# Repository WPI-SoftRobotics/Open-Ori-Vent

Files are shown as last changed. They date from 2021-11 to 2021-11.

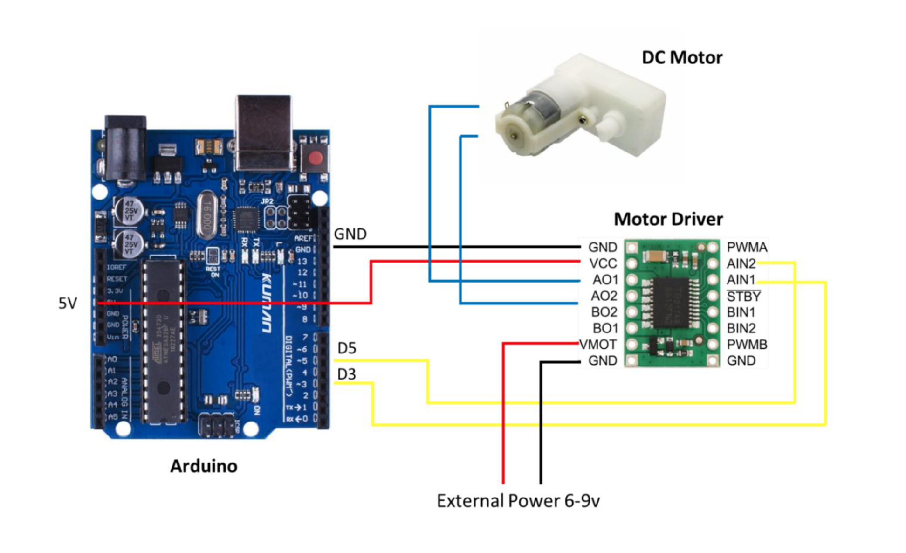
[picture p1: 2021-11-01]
images/wiring_diagram.png

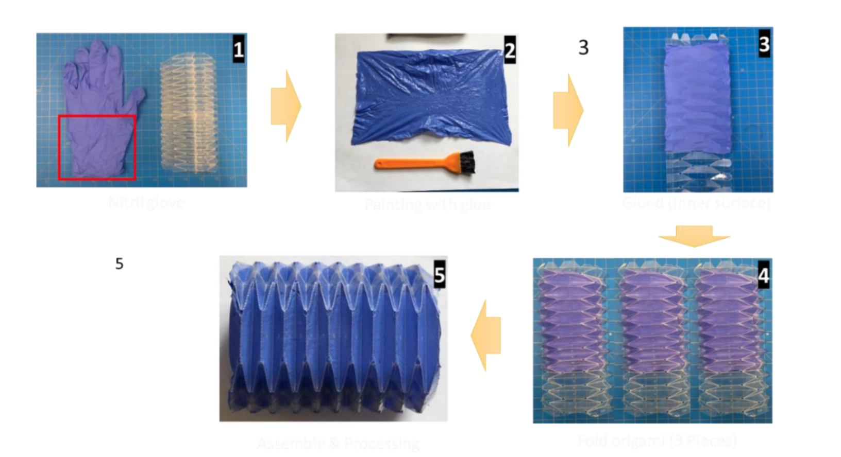
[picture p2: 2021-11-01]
images/sealing_method_2.png

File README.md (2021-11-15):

# Open-Ori-Vent: Portable Origami-Inspired Ventilators

The COVID-19 pandemic is responsible for hundreds of thousands of deaths
worldwide and remains a challenge that humanity must still overcome. As
hospitals continue to admit critical patients, they face medical
equipment shortages that may hinder life-saving treatments. We seek to
combat this equipment shortage by presenting a proof-of-concept portable
automated ventilator that is:

-   Low cost

-   Simple, Lightweight, Easy-to fabricate

As an open-source project, we are sharing all the CAD files as well
as the software. We hope that you can also make your own ventilator
using these instructions! For the current designs, laser cutters and 3d
printers are necessary, though these parts could be cut/printed
elsewhere and then mailed to you for assemble.

## Disclaimer
:warning: We would like include a warning and disclaimer here:

Please check the full disclaimer as well before proceeding.

* The material and documentation here is provided with no warranties explicit or implied.
* No material on this site is intended to provide medical advice. All designs are intended for investigational use only.
* This site does not represent any official policies or procedures.

The project is provided "as is", without warranty of any kind, express or implied, including but not limited to the warranties of merchantability, fitness for a particular purpose and noninfringement.

In no event shall the authors or copyright holders be liable for any claim, damages or other liability, whether in an action of contract, tort or otherwise, arising from, out of or in connection with the software or the use or other dealings in the software.

Only use **this repository, designs, documentation or any provided information** if you accept the above disclaimer.

## Citation:

Ori-Vent: Design and Prototyping of Accessible and Portable Origami-Inspired Ventilators

Please cite: 
> Aihaitijiang, Abudula, et al. "Ori-Vent: Design and Prototyping of Accessible and Portable Origami-Inspired Ventilators." *International Symposium on Experimental Robotics.* Springer, Cham, 2020.

WPI Soft Robotics Lab [softrobotics.wpi.edu](https://softrobotics.wpi.edu/)

Worcester Polytechnic Institute

## Materials and methods
See tutorials in our project [Wiki](https://github.com/WPI-SoftRobotics/Open-Ori-Vent/wiki). Or download ReadMe.pdf

## Download 

git clone the whole project or download .zip file (Include all Steps)

## Video

See here: [https://youtu.be/49nRoLKjMFs](https://youtu.be/49nRoLKjMFs)

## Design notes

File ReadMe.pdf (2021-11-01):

## Open-Source Project

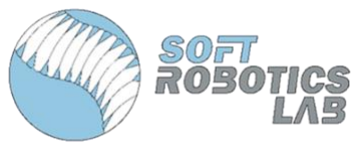
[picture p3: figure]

# Ori-Vent: Design and Prototyping of Accessible and Portable Origami-Inspired Ventilators

## Soft Robotics Lab

## Worcester Polytechnic Institute

Table of Contents

Introduction ------------------------------------------------------------------------------------ 2

Part 1: Materials ------------------------------------------------------------------------------- 2

Part 2: Printed Parts List --------------------------------------------------------------------- 3

Part 3: Building the Bellows ----------------------------------------------------------------- 4

Part 4: Sealing Bellows ----------------------------------------------------------------------- 5

Part 5: Wiring Diagram ----------------------------------------------------------------------- 6

Part 6: Assembly ------------------------------------------------------------------------------- 7

Part 7: Download Section --------------------------------------------------------------------7

Part 8: Video ------------------------------------------------------------------------------------ 7

Introduction:

The COVID-19 pandemic is responsible for hundreds of thousands of deaths worldwide and remains a challenge that humanity must still overcome. As hospitals continue to admit critical patients, they face medical equipment shortages that may hinder life-saving treatments. We seek to combat this equipment shortage by presenting a proof-of-concept portable automated ventilator that is:

- Low cost
- Simple, Lightweight, Easy-to fabricate

As an open-source project, we will made public all the CAD files as well as the software. We hope that you can also make your own ventilator using these instructions! For the current designs, laser cutters and 3d printers are necessary, though these parts could be cut/printed elsewhere and then mailed to you for assemble.

Part 1: Materials & Orders

The initial prototype uses inexpensive materials and is easy to manufacture. It is not necessary to buy or order same product as listed below. You can do substitutions from your own supplies or purchase similar items from somewhere else.

1 x Arduino | $10.69 | Order (https://www.amazon.com/kuman-Board-ATmega328P-Cable-Arduino/dp/B016D5KOOC?s=electronics) (Amazon)
1 x Jumper Wires | $3.95 | Order (https://www.amazon.com/Adafruit-Premium-Female-Extension-Jumper/dp/B011OCHYH4) (Amazon)
1 x Gear Motor | $5.75 | Order (https://www.robotshop.com/en/solarbotics-gm2-gear-motor-2-offset.html) (RobotShop)
1 x Motor Driver | $3.33 | Order (https://www.robotshop.com/en/pololu-dual-dc-motor-driver-1a-4-5v-3-5v-tb6612fng.html) (RobotShop)
1 x Pressure Sensor (optional) | $16.33 | Order (https://www.digikey.com/en/products/detail/nxp-usa-inc/mpx5010dp/464054) (Digi-Key)

For sealing origami bellows:

1 x *Stretchlon200 Bagging Film | $3.90 | Order (https://www.fibreglast.com/product/stretchlon-200-bagging-film-1678/Vacuum_Bagging_Films_Peel_Ply_Tapes) (FibreGlast)
1 x *Nitrile Exam Gloves (Optional) | - | Order (https://www.amazon.com/MedPride-Powder-Free-Nitrile-Gloves-Medium/dp/B00GS8W3T4) (Amazon)
1 x *E6000 Glue | $7.64 | Order (https://www.amazon.com/E6000-230010-Craft-Adhesive-Ounces/dp/B007TSYNG8) (Amazon)

Others:

1 x Screws | - | -
1 x *PET film | - | -
1 x One way valve (2 Pieces) | $6.69 | Order (https://www.amazon.com/Check-Valve-Inline-Return-Liquid/dp/B07CC9K599) (Amazon)
1 x Fishing wire | $2.99 | Order (https://www.amazon.com/Triple-Fish-Test-Leader-Fishing/dp/B01BZPPDJG?rnid=386589011) (Amazon)
1 x Rubber Tube | $8.59 | Order (https://www.amazon.com/Nydotd-Natural-Slingshot-Catapult-Surgical/dp/B07DL6JJZ2) (Amazon)

* Optional Part: Order if you want to make origami bellows.

Part 2: Printed Part List

Files: Open Source Ori-Vent\Printed Parts\.STL & .SLDPRT

Here is a list of all the parts that need to be printed:

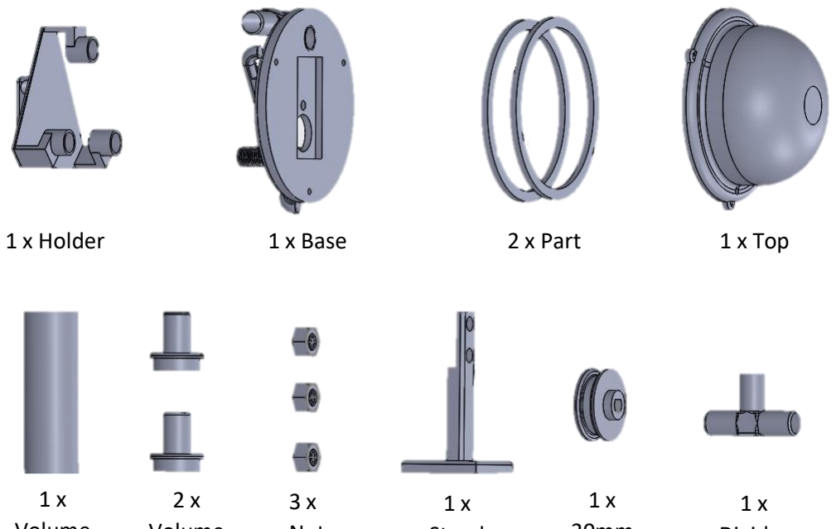
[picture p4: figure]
1 x Holder; 1 x Base; 2 x Part; 1 x Top

Print Settings

Profile Default: High resolution

Supports: Yes

Infill: 60%+

Filament material: PLA

Volume
Tube

Volume
(in&out)

Nut
Stand

30mm
Spool

Divider

Part 3: Building the Bellows

Origami Bellows:

Files: Open Source Ori-Vent\Origami_Laser Cut\.DXF

Quantity: 3 x Origami Pattern

Material: PET (Polyethylene Terephthalate) or any other low-cost and accessible plastic

Note: We provide two different length of origami patterns (18 inch and 9)

3D Printed Bellows

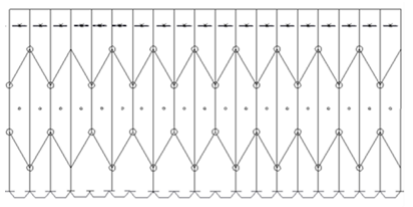
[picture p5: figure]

Files: Open Source Ori-Vent \ 3D Printed Bellows \ .SLDPRT:

Print Settings

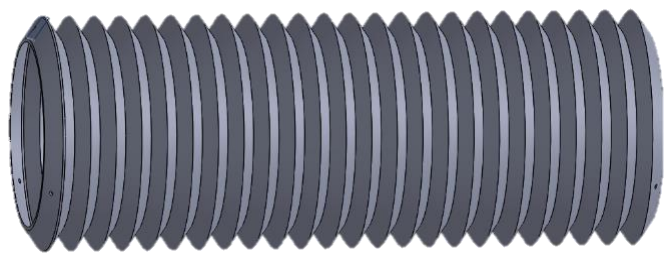
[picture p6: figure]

Profile Default: High resolution, insure at least two layers for

Supports: No

Filament material: NinjaFlex

Part 4: Sealing Origami Bellows

To seal the holes within the origami structure, we tested two different materials and sealing processes. We recommend sealing with bagging film.

1) Origami Bellows Sealing Process (recommended): You can glue (E6000 flexible glue) the Stretchlon200 bagging film to the inner surface of the assembled origami module before folding completely.

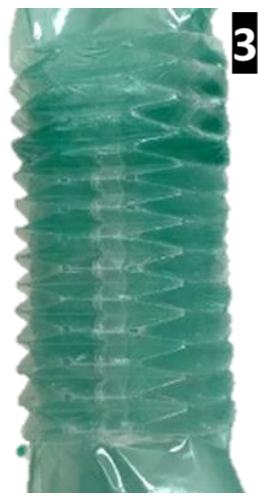
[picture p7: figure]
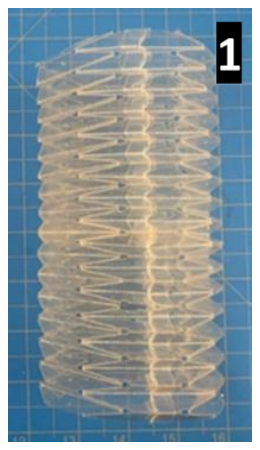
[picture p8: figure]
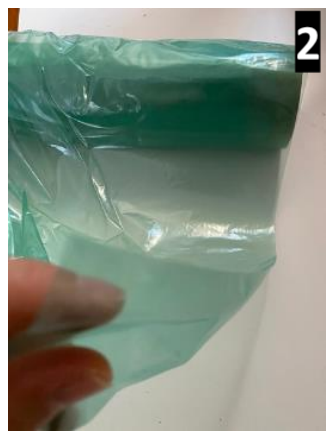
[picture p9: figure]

2) Origami Bellows Sealing Process (Optional): You can glue multiple pieces of Nitrile exam glove onto the inner surface of the unfolded origami module using E6000 flexible glue. Lastly, assemble all 3 origami pieces and glue attached sections.

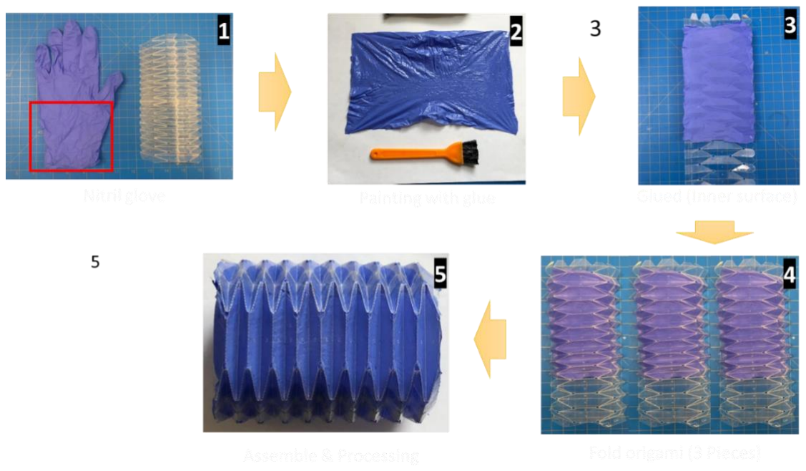
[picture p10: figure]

Part 5: Wiring Diagram

Minimal wiring diagram for connecting a microcontroller to a motor driver. You can use breadboard (optional) or solder pins on the motor driver.

Files: Open Source Ori-Vent\Code&Data\Arduino\.ino

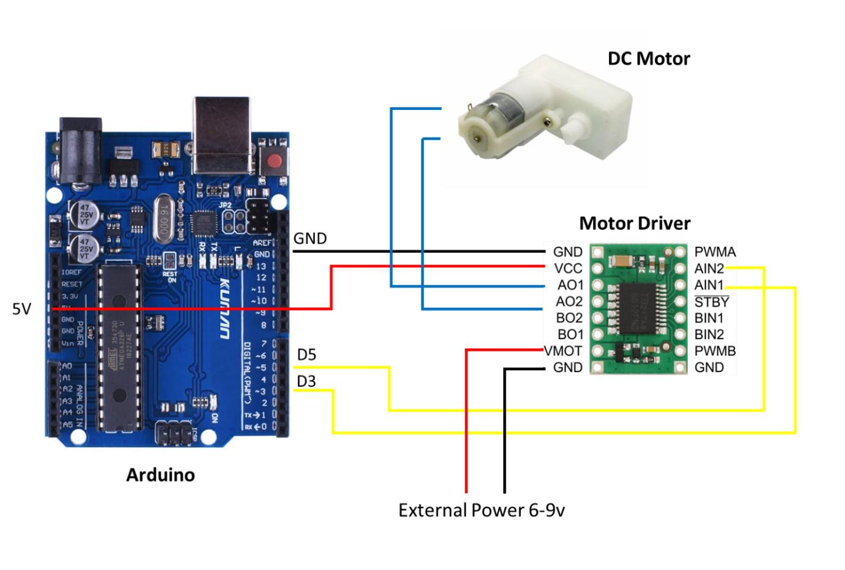
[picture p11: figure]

Micro Controller | Motor Driver

GND ----------------------------> GND

5V ----------------------------> VCC

D3 ----------------------------> AIN1

D5 ----------------------------> AIN2

Part 6: Assembly

Assemble printed parts from Part 1 and sealed/3D printed bellows.

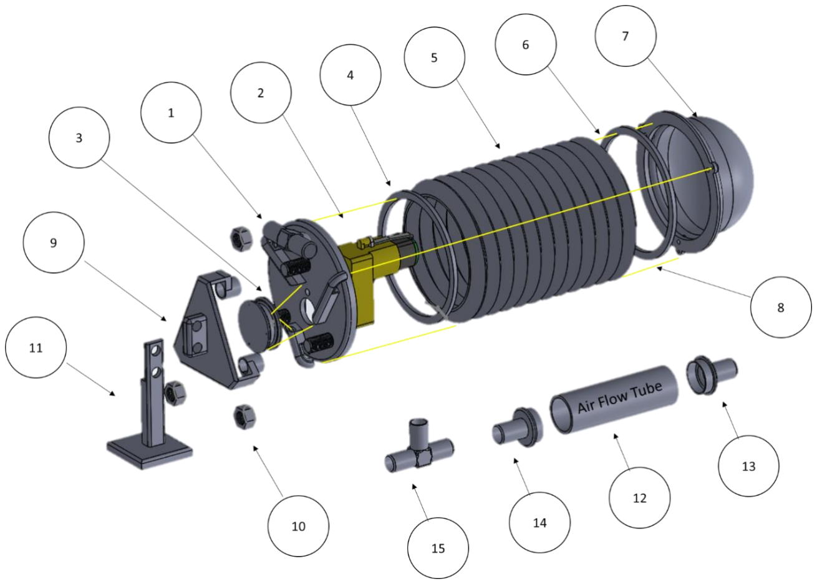
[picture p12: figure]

①-②Attach the motor and mount to the 3d printed part. ③Mount spool. ④-⑥ Origami/3D printed bellows. ⑦Back cover. ⑧ Wraps the cables around a spool and attached to the other end. ⑨Holder. ⑩Nuts. ⑪Mount stand. ⑫-⑮Assemble air flow tube (optional).

Part 7: Download Section

Download .zip file (Include all Steps)

Part 8: Video

Files: Open Source Ori-Vent \ Video \ .mp4

YouTube Link:

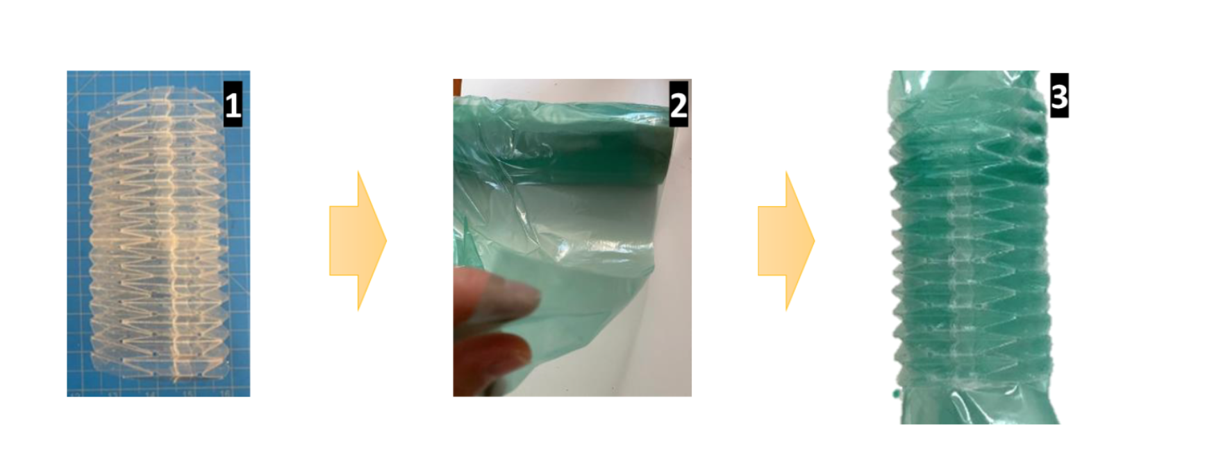
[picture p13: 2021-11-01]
images/sealing_method_1.png

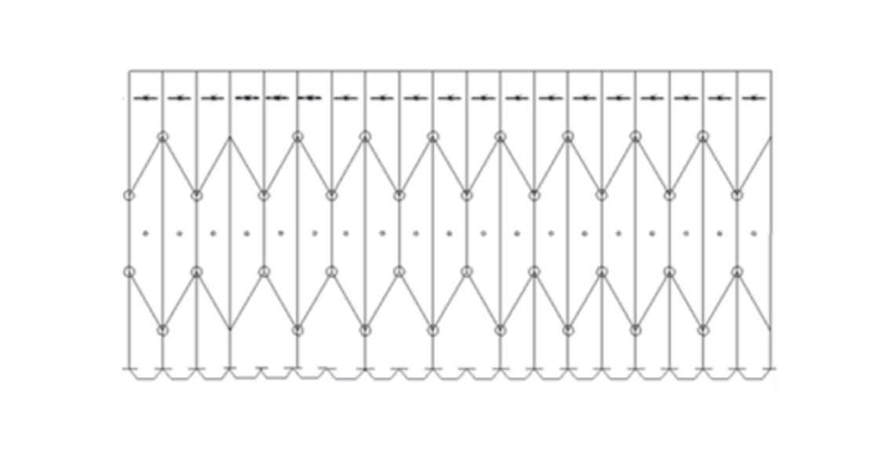
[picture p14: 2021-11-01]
images/bellows_pattern_for_laser_cutting.png

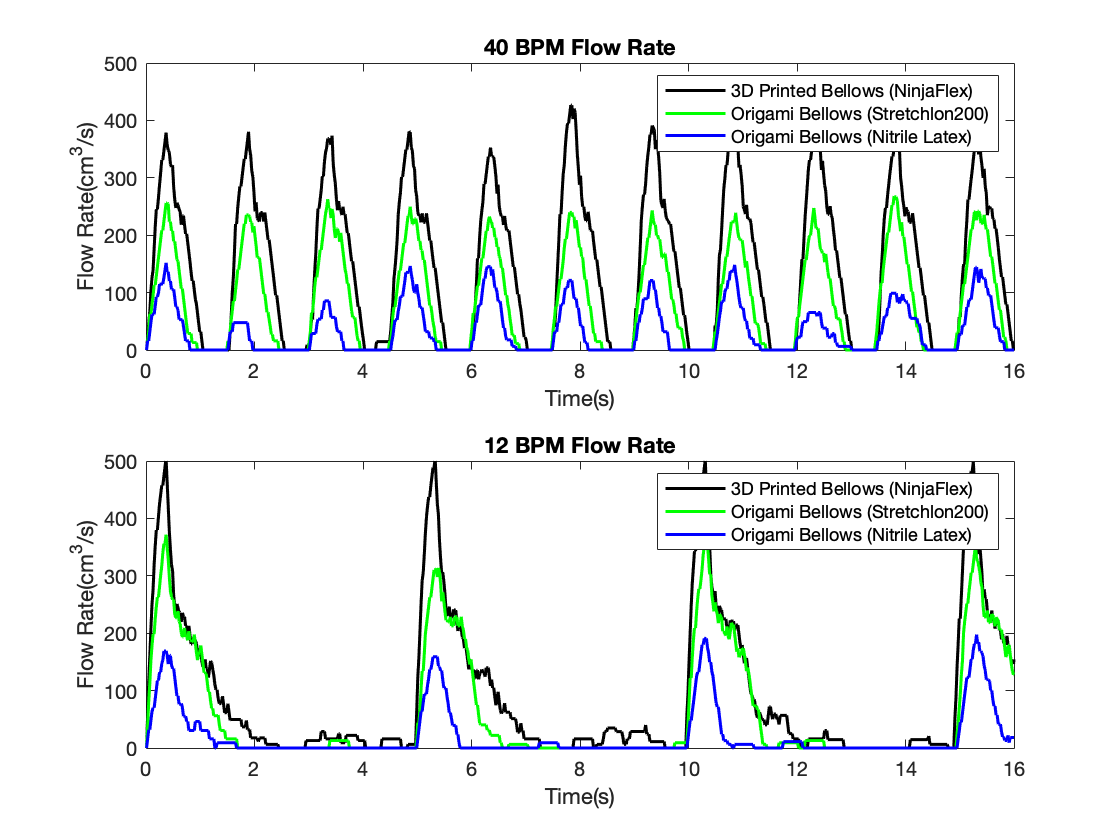
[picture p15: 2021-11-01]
Code&Data/Matlab_Data/flowrate_2x1.png

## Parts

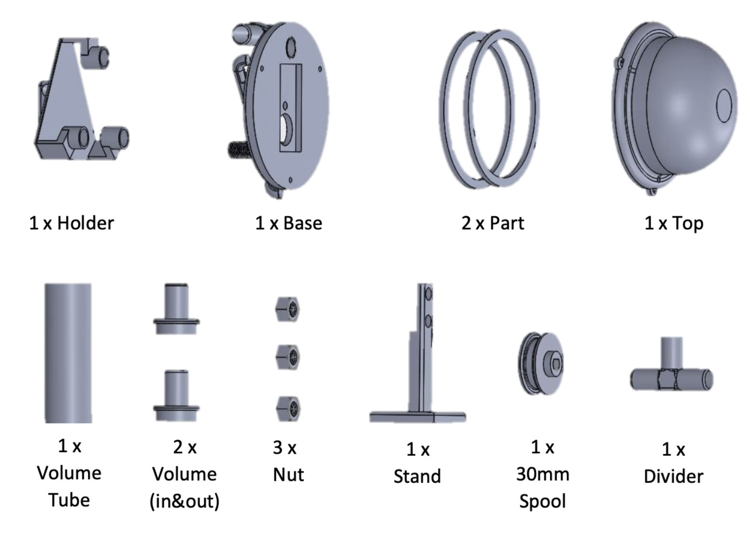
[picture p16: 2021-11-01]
images/printed_part_list.png

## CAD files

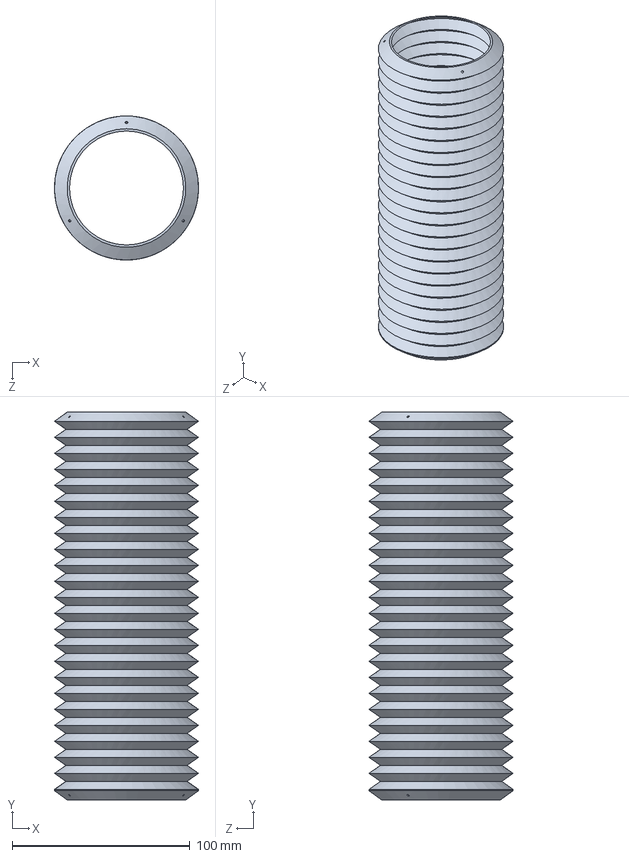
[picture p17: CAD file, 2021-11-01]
3D Printed Bellows/SoftBellows(long).SLDPRT
81.0 x 218.2 x 81.1 mm

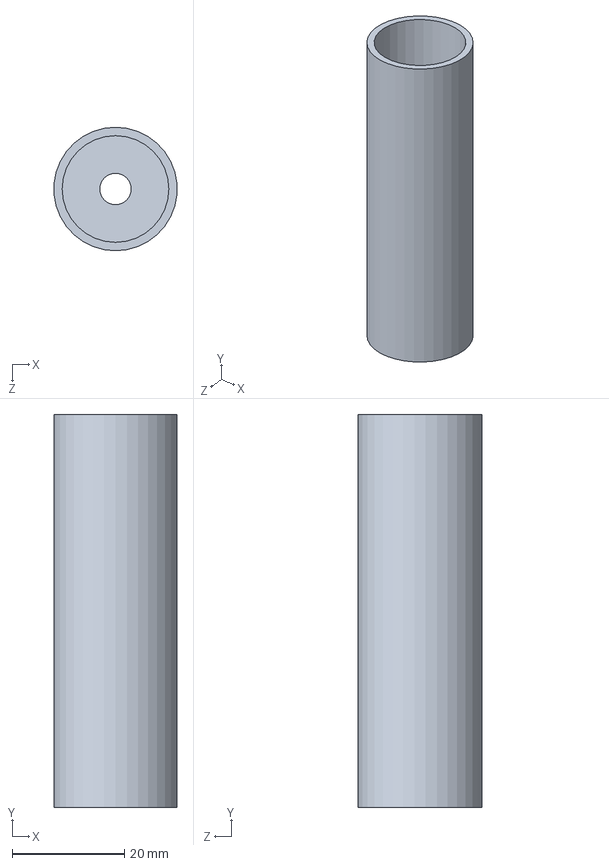
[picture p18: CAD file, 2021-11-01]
Code&Data/Arduino/Reference&Backup/Volume Sensor 3D Part/Volume1.SLDPRT
21.9 x 70.0 x 22.0 mm

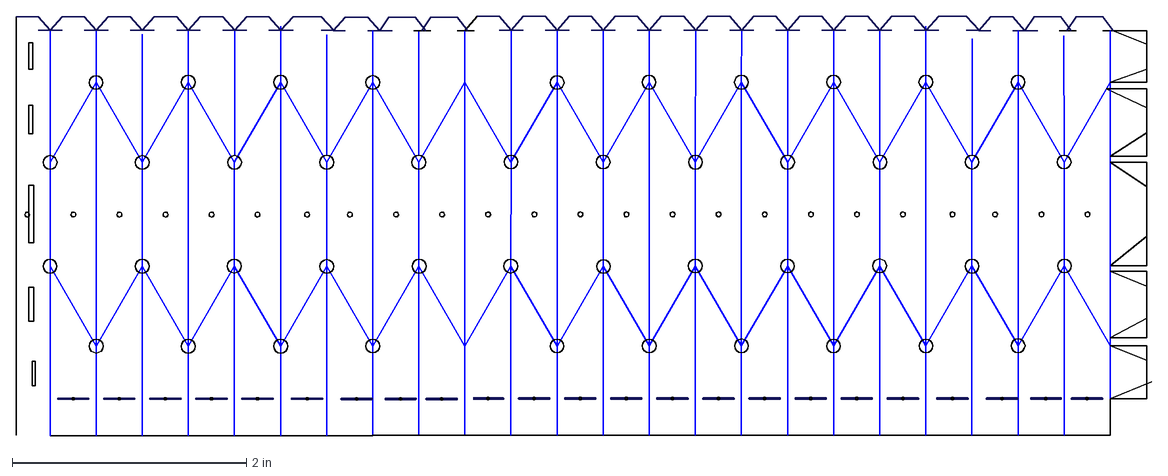
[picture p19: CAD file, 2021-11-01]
Origami_Laser Cut/6_Assamble_Cut.dxf
9.70 x 3.58 in

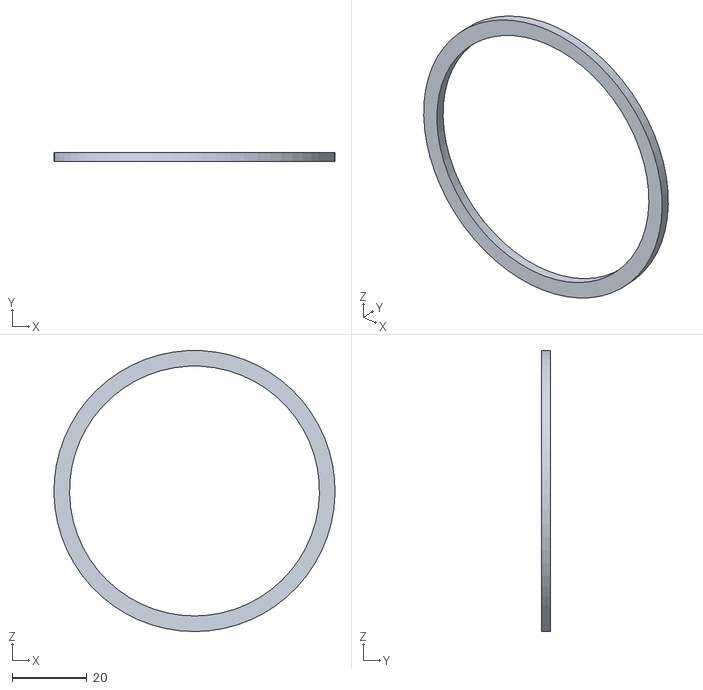
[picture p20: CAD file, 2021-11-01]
Printed Parts/part_stl.STL
75.0 x 2.50 x 75.1

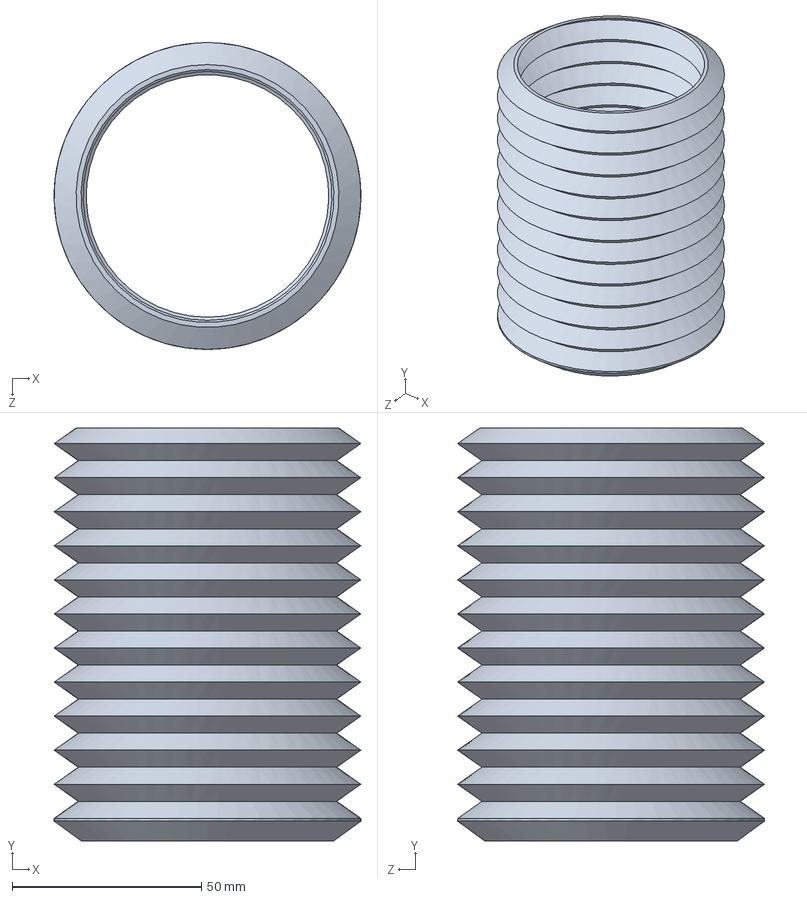
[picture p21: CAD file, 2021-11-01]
3D Printed Bellows/SoftBellows_115mm.SLDPRT
81.0 x 109.1 x 81.1 mm

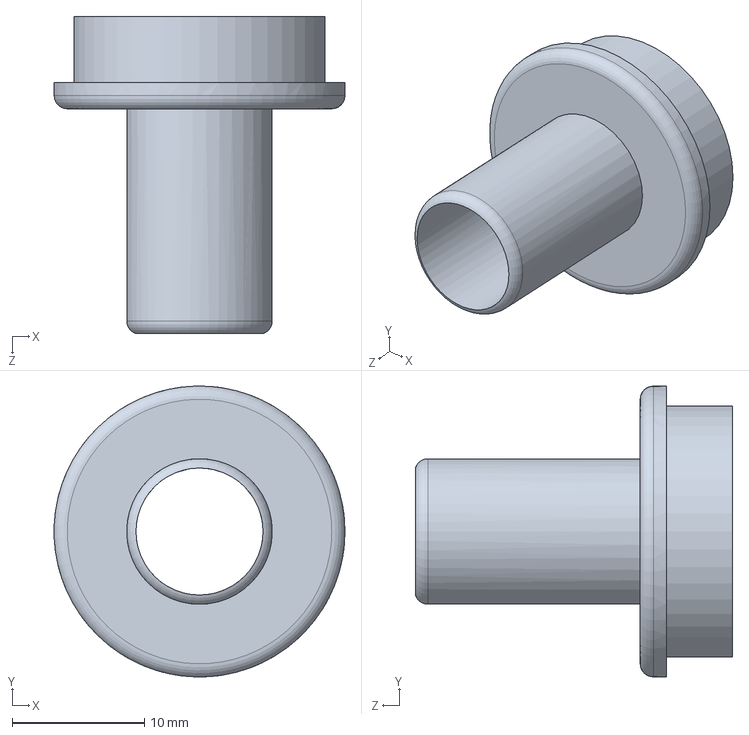
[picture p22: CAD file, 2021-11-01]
Code&Data/Arduino/Reference&Backup/Volume Sensor 3D Part/Volume2.SLDPRT
22.0 x 22.0 x 24.0 mm

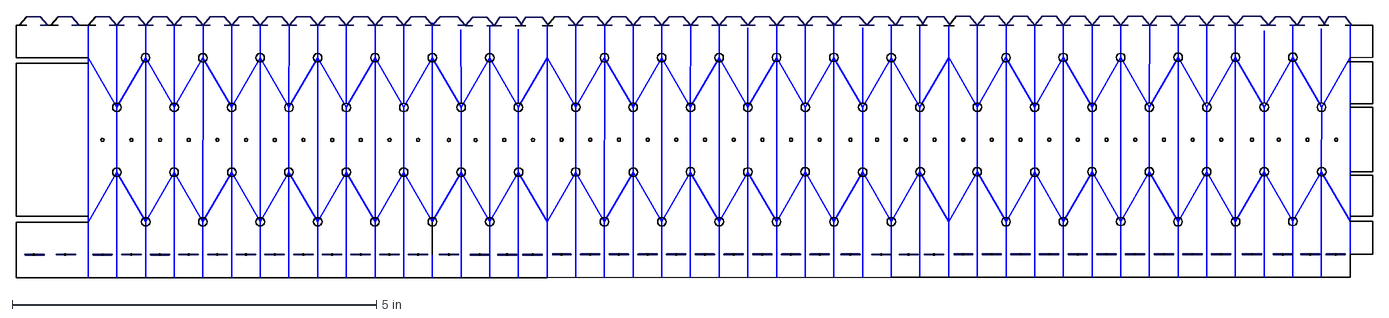
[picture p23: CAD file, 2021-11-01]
Origami_Laser Cut/3Sides_Assamble_6Pices(Short).dxf
18.6 x 3.58 in

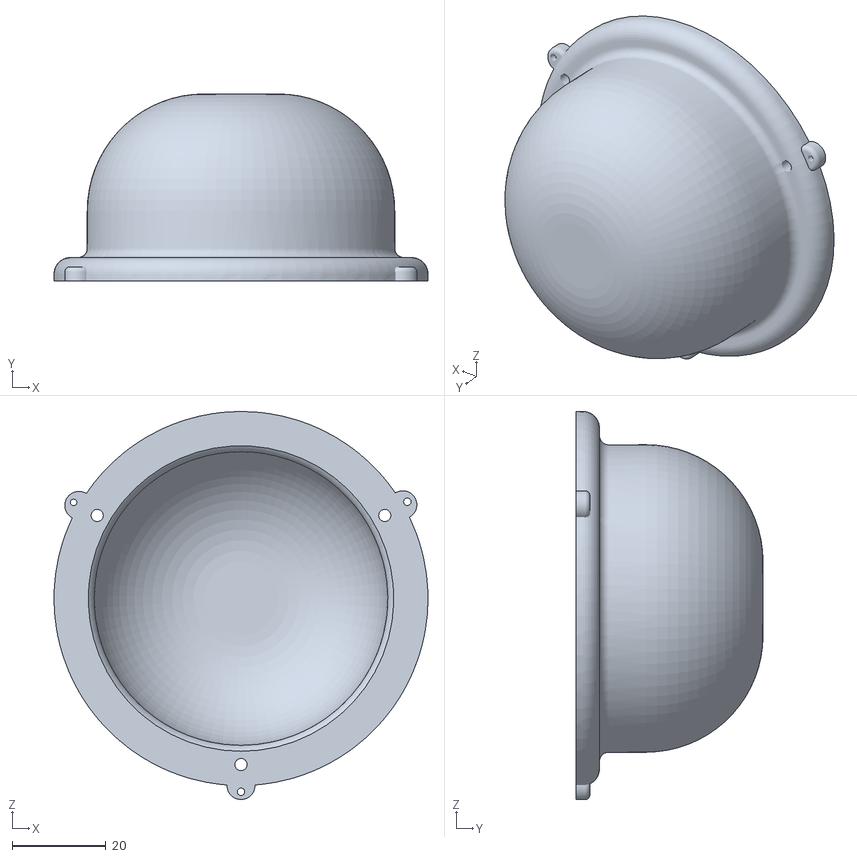
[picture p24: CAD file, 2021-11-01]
Printed Parts/Top_stl.STL
80.0 x 40.0 x 83.0

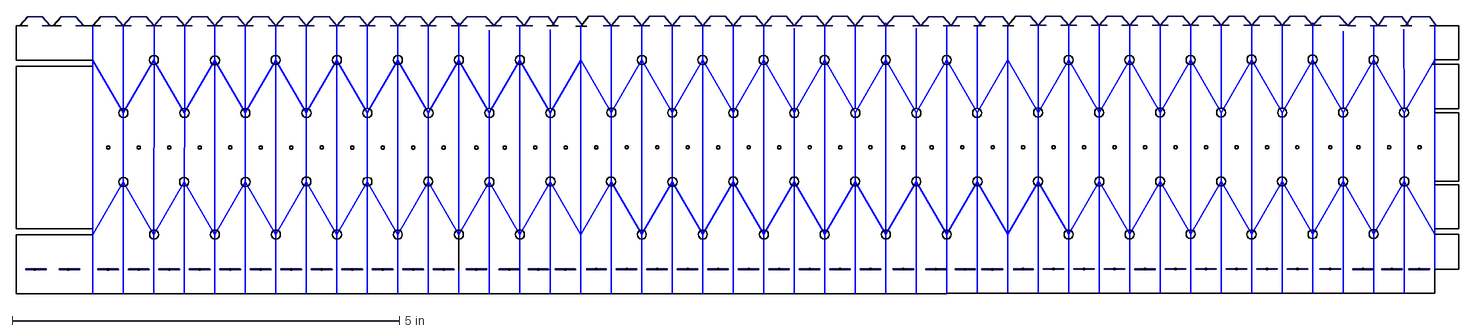
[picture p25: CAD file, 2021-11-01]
Origami_Laser Cut/3Sides_18inch_Ready_Cut(Long).dxf
18.6 x 3.58 in

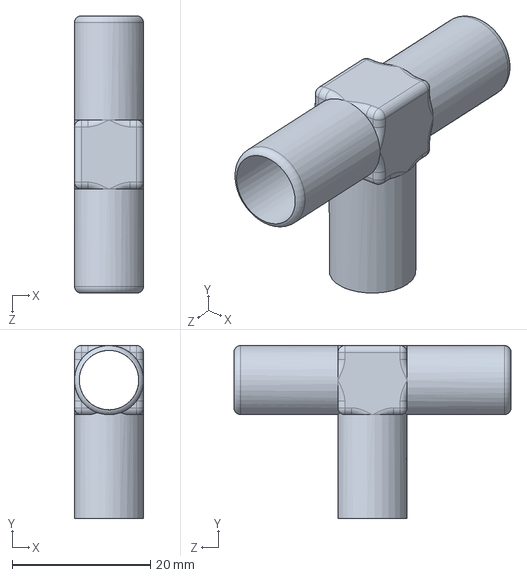
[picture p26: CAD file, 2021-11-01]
Printed Parts/Divider (Tube).SLDPRT
10.0 x 25.0 x 40.0 mm

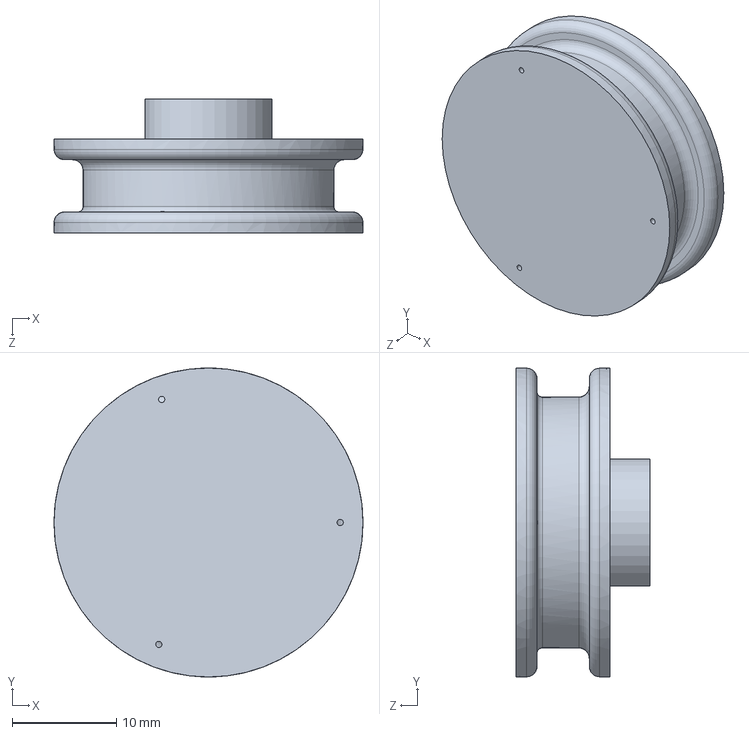
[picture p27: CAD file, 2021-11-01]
Printed Parts/30mm Spool.SLDPRT
29.6 x 29.6 x 12.8 mm

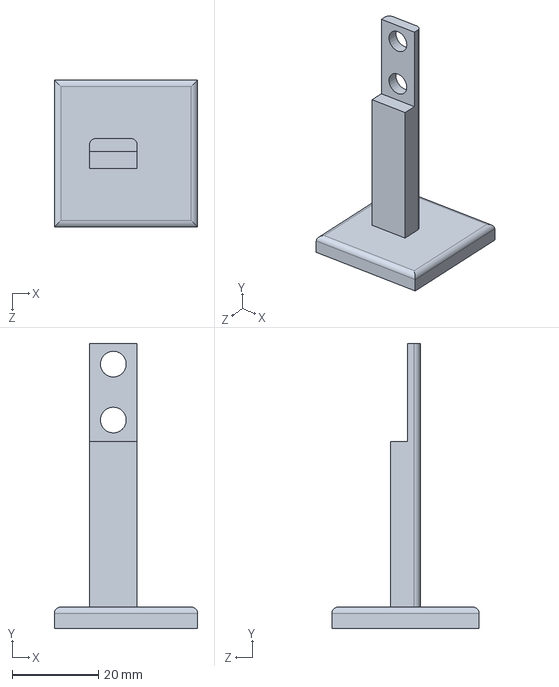
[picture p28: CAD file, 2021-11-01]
Printed Parts/stand.SLDPRT
33.3 x 66.3 x 34.3 mm

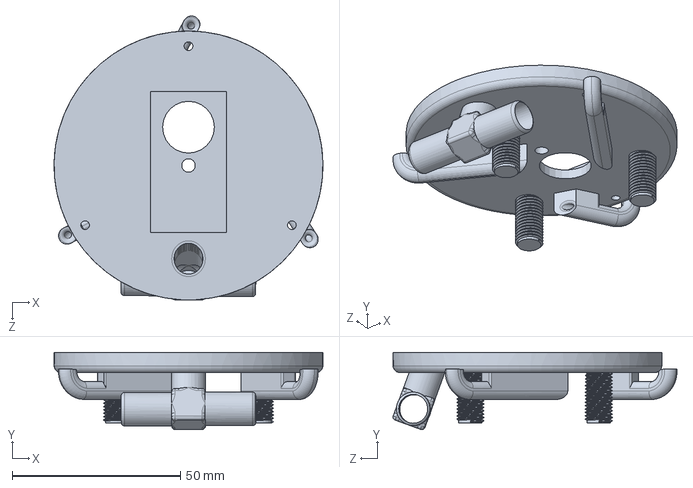
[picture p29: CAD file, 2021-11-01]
Printed Parts/Base.SLDPRT
80.0 x 23.0 x 84.5 mm

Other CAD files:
Printed Parts/Top.SLDPRT
Printed Parts/stand_stl.STL
Printed Parts/part.SLDPRT
Code&Data/Arduino/Reference&Backup/Volume Sensor 3D Part/Volume1.STL
Code&Data/Arduino/Reference&Backup/Volume Sensor 3D Part/Volume2.STL
Printed Parts/30mm Spool.STL
Printed Parts/Base.STL
Printed Parts/Divider (Tube).STL
Printed Parts/Nut.SLDPRT
Printed Parts/Nut_stl.STL
Printed Parts/Volume (in&out).STL
Printed Parts/VolumeTube.STL

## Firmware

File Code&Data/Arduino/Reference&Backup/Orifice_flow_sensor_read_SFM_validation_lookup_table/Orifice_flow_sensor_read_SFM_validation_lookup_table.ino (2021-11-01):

/*
   Reading flow rate from DIY orifice flow sesnor. This code reads from the following sensors and outputs
   data to the serial terminal which can be copied into notepad and saved as a .csv file for importing into Excel:
   - Reads flow rate from the DIY orifice flow sensor based on a lookup table (will need recalibrating for your test rig)
     (not compensated for temperature or downstream pressure)
   - Reads the sensirion SFM3300 sensor over i2c for calibration purposes
  Code written by Darren Lewis, May 2020
*/

//#include <avr/pgmspace.h>      // for flash storage
#include <Wire.h>              // needed for SFM

int offset = 32768;            // SFM Offset for the SFM3300, check datasheet if you're using a different sensor
int scale = 120;               // SFM Scale

#define orificeSensorPin A0    // connection pin for MPX5010DP



// ADC count, flow (ml/s) lookup table MPX5010DP
int flowArray[644] = {
  0
  , 0
  , 0
  , 0
  , 0
  , 0
  , 0
  , 0
  , 0
  , 0
  , 0
  , 0
  , 0
  , 0
  , 0
  , 0
  , 0
  , 0
  , 0
  , 0
  , 0
  , 0
  , 0
  , 0
  , 0
  , 0
  , 0
  , 0
  , 0
  , 0
  , 0
  , 0
  , 0
  , 0
  , 0
  , 0
  , 0
  , 159
  , 166
  , 177
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
};



const float ADC_mV = 4.8828125;      // convesion multiplier from Arduino ADC value to voltage in mV
const float sensitivity = 4.413;     // in mV/mmH2O taken from datasheet
const float mmh2O_cmH2O = 10;        // divide by this figure to convert mmH2O to cmH2O
const float mmh2O_kpa = 0.00981;     // convesion multiplier from mmH2O to kPa
const float mmh2O_pa = 9.80665;      // convesion multiplier from mmH2O to Pa
const int ADCoffset = 34;            // measured from Arduino when rig is off. Valid for MPX5010DP
// the offset value from the datasheet I found was too high at atmospheric, that's why I used a measured value for offset

void setup() {
  //Wire.begin();
  delay(500); // let serial console settle
  Serial.begin(9600);

  // initialize the sesnor
  //measflow.init();
  Serial.println("Sensor initialized!");
}

void loop() {
  // for reading the raw pressure values of the orifice flow senror
  int rawValue = analogRead(orificeSensorPin);
  float zeroedADCval = float(rawValue) - ADCoffset;                    // normalise readings with the offset
  zeroedADCval = constrain(zeroedADCval, 0, 1023);
  float pressurePa = zeroedADCval * ADC_mV / sensitivity * mmh2O_pa;  // result in Pa use this line when using ADCoffset


 // for reading home made orifice sensor flow rate from lookup table
  int flowRate = flowArray[rawValue];       // ml/s

 // Serial.print(millis());           // record time in ms
 // Serial.print(" , ");              // needed to create .csv file
  Serial.print(rawValue);           // raw ADC value
  Serial.print(" , ");
  Serial.print(pressurePa);         // reading of differential pressure over the orifice
  Serial.print(" , ");
  Serial.println(flowRate);           // flow rate reading from orifice sensor

  // using serial print format above, you can copy your data from the arduino terminal,
  // paste it into NotePad app, than save as a .CSV file which can be opened in Excel

// to use the serial plotter (under tools menu); uncomment serial prints below and comment out serial prints above

//  Serial.print(rawValue);           // raw ADC value
//  Serial.print("  ");
//  Serial.print(pressurePa);         // reading of differential pressure over the orifice
//  Serial.print("  ");
//  Serial.print(flowRate);           // flow rate reading from orifice sensor
//  Serial.print("  ");
//  Serial.print(flowSFM);            // flow rate reading from SFM3300 sensor
//  Serial.print("  ");
//  Serial.println("uT");

 delay(100);     // uncomment this delay to make it easier to read number to the screen
}

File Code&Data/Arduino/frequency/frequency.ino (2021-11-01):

// Ventilator motor set clockwise
int Vent1_clockwise = 3;      // Bellows 1 connected to Analog pin 3
int Vent2_clockwise = 6;      // Bellows 2 connected to Analog pin 3
int Vent3_clockwise = 9;      // Bellows 3 connected to Analog pin 3

// Ventilator motor set counterclockwise
int Vent1_counterclockwise = 5;      // Bellows 1 connected to Analog pin 3
int Vent2_counterclockwise = 10;      // Bellows 2 connected to Analog pin 3
int Vent3_counterclockwise = 11;      // Bellows 3 connected to Analog pin 3

void setup() {
  pinMode(Vent1_clockwise, OUTPUT);  // sets the pin as output
  pinMode(Vent2_clockwise, OUTPUT);  // sets the pin as output
  pinMode(Vent3_clockwise, OUTPUT);  // sets the pin as output
  pinMode(Vent1_counterclockwise, OUTPUT);  // sets the pin as output
  pinMode(Vent2_counterclockwise, OUTPUT);  // sets the pin as output
  pinMode(Vent3_counterclockwise, OUTPUT);  // sets the pin as output  
}

void loop() {


// Robustness test   0.5 Hz
/*
  // 12 Breaths per minute    5(S)  
  //analogWrite(Vent1_clockwise,255); // analogRead values go from 0 to 1023, analogWrite values from 0 to 255
  analogWrite(Vent3_clockwise,255);
  delay(1000);//1000

  //analogWrite(Vent1_counterclockwise,0); // analogRead values go from 0 to 1023, analogWrite values from 0 to 255
  analogWrite(Vent3_clockwise,0);
  delay(1000);
*/



  // 12 Breaths per minute    5(S)  
  analogWrite(Vent1_clockwise,255); // analogRead values go from 0 to 1023, analogWrite values from 0 to 255
  analogWrite(Vent2_clockwise,255);
  analogWrite(Vent3_clockwise,255);
  delay(1000);//1000
  analogWrite(Vent1_clockwise,0); // analogRead values go from 0 to 1023, analogWrite values from 0 to 255
  analogWrite(Vent2_clockwise,0);
  analogWrite(Vent3_clockwise,0);
  delay(50);
  analogWrite(Vent1_counterclockwise,255); // analogRead values go from 0 to 1023, analogWrite values from 0 to 255
  analogWrite(Vent2_counterclockwise,255);
  analogWrite(Vent3_counterclockwise,255);
  delay(50);//1000
  analogWrite(Vent1_counterclockwise,0); // analogRead values go from 0 to 1023, analogWrite values from 0 to 255
  analogWrite(Vent2_counterclockwise,0);
  analogWrite(Vent3_counterclockwise,0);
  delay(3900);

  
/*
  // 40 breaths per minute    1.5(S) 

  analogWrite(Vent1_clockwise,255); // analogRead values go from 0 to 1023, analogWrite values from 0 to 255
  analogWrite(Vent2_clockwise,255);
  analogWrite(Vent3_clockwise,255);
  delay(1000);//1000
  analogWrite(Vent1_clockwise,0); // analogRead values go from 0 to 1023, analogWrite values from 0 to 255
  analogWrite(Vent2_clockwise,0);
  analogWrite(Vent3_clockwise,0);
  delay(50);
  analogWrite(Vent1_counterclockwise,255); // analogRead values go from 0 to 1023, analogWrite values from 0 to 255
  analogWrite(Vent2_counterclockwise,255);
  analogWrite(Vent3_counterclockwise,255);
  delay(50);//1000
  analogWrite(Vent1_counterclockwise,0); // analogRead values go from 0 to 1023, analogWrite values from 0 to 255
  analogWrite(Vent2_counterclockwise,0);
  analogWrite(Vent3_counterclockwise,0);
  delay(400);

*/
  
}

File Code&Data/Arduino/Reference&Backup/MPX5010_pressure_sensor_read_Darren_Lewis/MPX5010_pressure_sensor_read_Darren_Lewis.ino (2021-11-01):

/*
  Darren Lewis calculated pressure readings MPX5010 baed on datasheet
  datasheet: https://docs.rs-online.com/9979/0900766b8138443c.pdf
  my website: http://darrenlewismechatronics.co.uk/
*/
const float ADC_mV = 4.8828125;       // convesion multiplier from Arduino ADC value to voltage in mV
const float SensorOffset = 200.0;     // in mV taken from datasheet
const float sensitivity = 4.413;      // in mV/mmH2O taken from datasheet
const float mmh2O_cmH2O = 10;         // divide by this figure to convert mmH2O to cmH2O
const float mmh2O_kpa = 0.00981;      // convesion multiplier from mmH2O to kPa

void setup() {
  Serial.begin(9600);
}

void loop() {
  // ((sensorValue in mV -sensorOffset)/sensitivity in mV/mmH2O)*kPa conversion constant
  //float sensorValue = ((analogRead(A0) * ADC_mV - SensorOffset) / sensitivity * mmh2O_kpa);     // result in kPa
  float sensorValue = (analogRead(A0) * ADC_mV - SensorOffset) / sensitivity / mmh2O_cmH2O;       // result in cmH2O

 // Serial.print(millis());
  Serial.print(" , ");
  Serial.println(sensorValue, 2);
  // using serial print format above, you can copy your data from the terminal,
  // paste it into NotePad app, than save as a .CSV file which can be opened in Excel
}
